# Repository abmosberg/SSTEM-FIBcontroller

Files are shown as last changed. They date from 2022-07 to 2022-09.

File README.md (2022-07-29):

# SSTEM-FIBcontroller
This is the public repository with all source files needed to reproduce the SuperSTEM FIBcontroller as presented at M&M2022.

## Notes on SuperSTEM FIBcontroller 1.0 and 1.1
The difference between revisions 1.0 and 1.1 is that in 1.0 KEY11, the bottom left button, does not work as it is connected to a pin that also connects to an LED, and thus the internal pullup behavior does not work well.
Version 1.1 attempts to fix this by moving KEY11 to D1 instead of D17.

This repository contains 3 folders, with different parts of the project:

### Arduino
Arduino sketch required to program the controller. See the Arduino help pages for instructions on how to flash. The Arduino Micro can be connected directly to a PC and flashed over the micro-USB cable.

Note, this code is still for v1.0, and is very much a rough first attempt, that can easily be refined.

### Enclosure
3D files, both Autodesk Inventor part files (configurable) and exported .stl files that can be read by any common slicer for 3D printing. For the prototype, .stl's were sliced in Ultimaker Cura and printed on an Ender 3 without supports.

### PCB
The subfolders FIBcontroller_v1.0 and v1.1 contain archived KiCad 6.0 projects. These should contain everything needed to iterate on the design, but for simple fabrication the accompanying gerber zip folders can be uploaded to any of the popular PCB manufacturing houses (e.g. PCBway, JLCPCB). v1.0 fabricated successfully to become the prototype, but no guarantees are given for v1.1
(it should only be a small change, so fairly safe)

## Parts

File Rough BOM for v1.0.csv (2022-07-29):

Type | Manufacturer | PartNo | Farnell Order Code | DigiKey PartNo | Number | Unit Price | Cost | Link
Arduino | Arduino | A000053 | 2285194 | 1050-1066-ND | 1 | £16.00 | £16.00 | https://www.digikey.co.uk/en/products/detail/arduino/A000053/4486332
Keyswitches - MX Black | Cherry | MX1A-11NW | 2292961 | CH160-ND | 14 | £0.71 | £9.91 | https://www.digikey.co.uk/en/products/detail/cherry-americas-llc/MX1A-11NW/91134
ALTERNATIVE
Keyswitches - MX Blue | Cherry | MX1A-E1NW | N/A | CH197-ND | 14 | £0.76 | £10.64 | https://www.digikey.co.uk/en/products/detail/cherry-americas-llc/MX1A-E1NW/20180
Keycaps | Adafruit | 5039 | N/A | 1528-5039-ND | 2 | £3.96 | £7.92 | https://www.digikey.co.uk/en/products/detail/adafruit-industries-llc/5039/14313478
Rotary encoder | Bourns | PEC11R-4215F-S0024 | 2474844 | PEC11R-4215F-S0024-ND | 2 | £1.66 | £3.32 | https://www.digikey.co.uk/en/products/detail/bourns-inc/PEC11R-4215F-S0024/4499665
Toggle switch | TE Connectivity ALCOSWITCH Switches | 1-1825137-6 | 3406889 | 450-2381-ND | 1 | 3.54 | 3.54 | https://uk.farnell.com/alcoswitch-te-connectivity/1-1825137-6/toggle-switch-spdt-5a-120v/dp/3406889
3-pin terminal block | Phoenix Contact | 1729131 | 1729131 |  | 1 | 0.976 | 0.976 | https://uk.farnell.com/phoenix-contact/1729131/terminal-block-wire-to-brd-3pos/dp/3041451
4-pin terminal block | Phoenix Contact | 1729144 | 3041475 |  | 1 | 1.12 | 1.12 | https://uk.farnell.com/phoenix-contact/1729144/terminal-block-wire-to-brd-4pos/dp/3041475
10k resistors | Multicomp pro | MCF 0.5W 10K | 9338373 |  | 5 | £0.06 | 0.2975 | https://uk.farnell.com/multicomp/mcf-0-5w-10k/res-10k-5-500mw-axial-carbon-film/dp/9338373
10nF axial capacitors | Vishay | MKT1813310635G | 1166871 |  | 2 | £1.05 | 2.1 | https://uk.farnell.com/vishay/mkt1813310635g/cap-0-01-f-630v-10-pet/dp/1166871
 |  |  |  |  |  | SUM: | £53.43

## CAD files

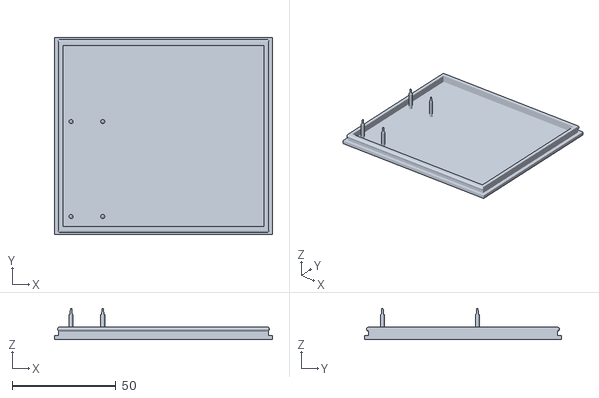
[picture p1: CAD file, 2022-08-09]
Enclosure/BARB_bottom_standalone.stl
105.0 x 95.0 x 15.0

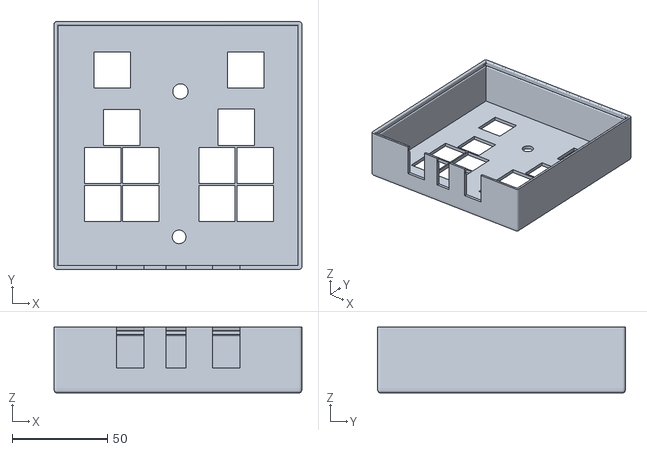
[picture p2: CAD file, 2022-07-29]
Enclosure/Enclosure_top_v2.stl
130.0 x 130.0 x 34.5

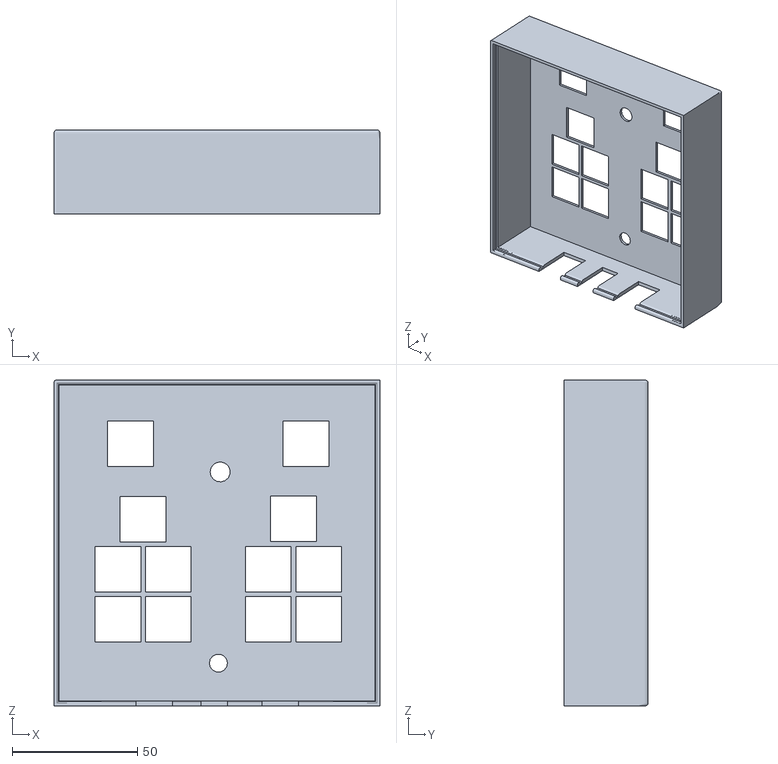
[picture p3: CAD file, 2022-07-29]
Enclosure/Enclosure_top.stl
130.0 x 33.5 x 130.0

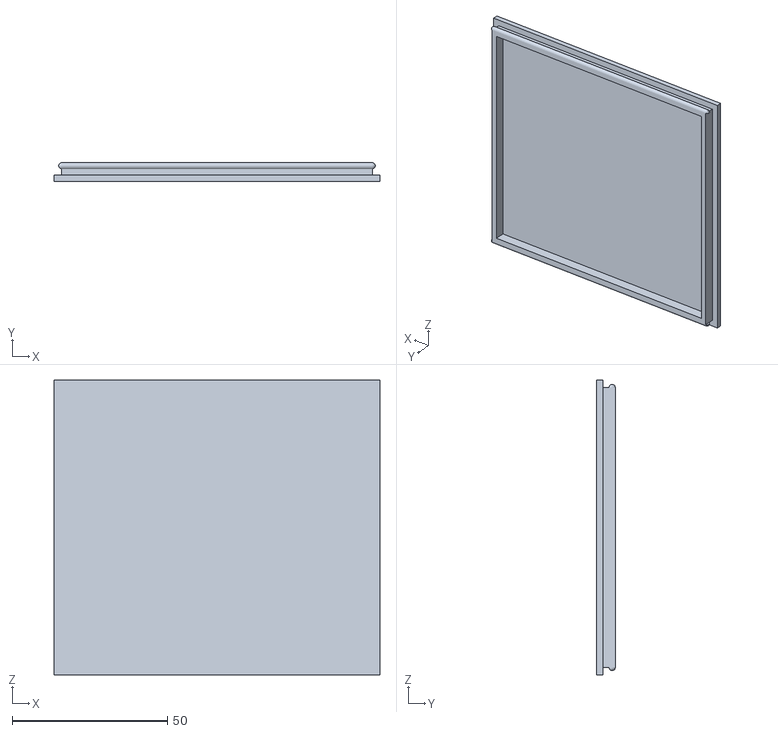
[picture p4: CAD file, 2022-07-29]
Enclosure/BRB_bottom_0.4mm_margin.stl
105.0 x 6.00 x 95.0

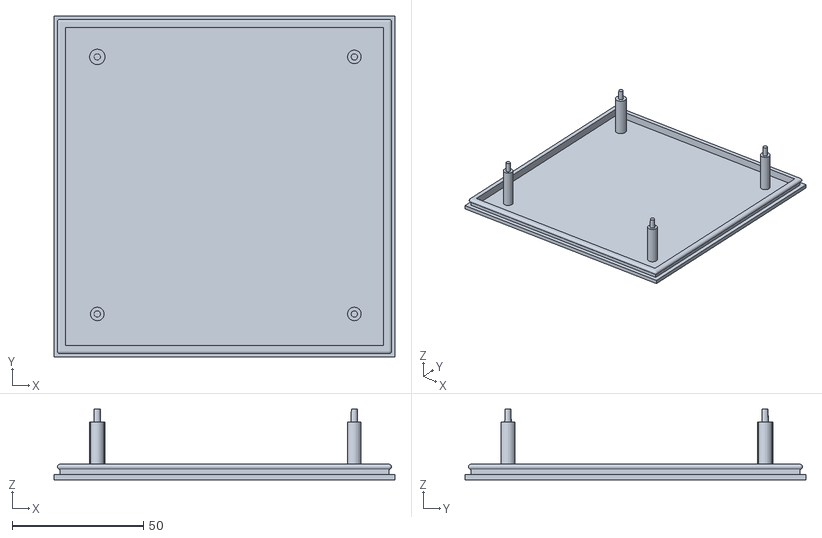
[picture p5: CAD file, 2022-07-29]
Enclosure/Enclosure_bottom_0.3mm_margin.stl
130.0 x 130.0 x 27.0

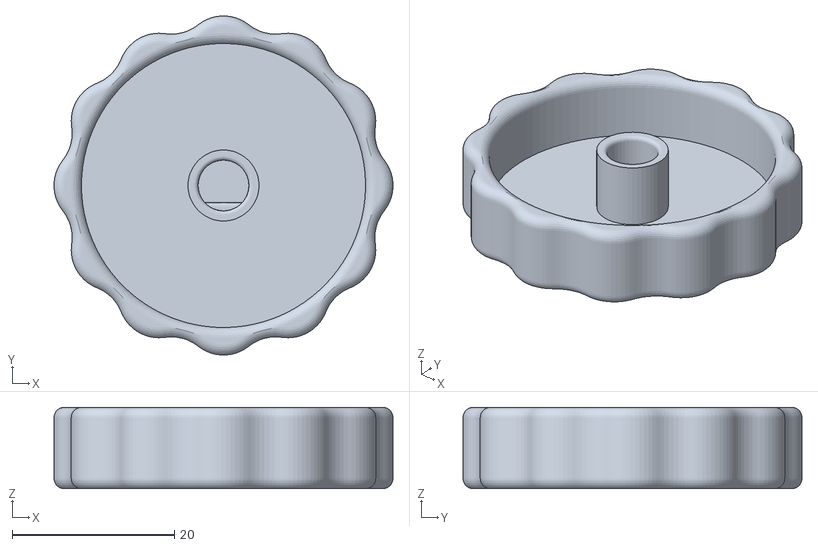
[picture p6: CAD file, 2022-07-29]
Enclosure/Encoder_wheel_10mm.stl
41.8 x 41.8 x 10.0

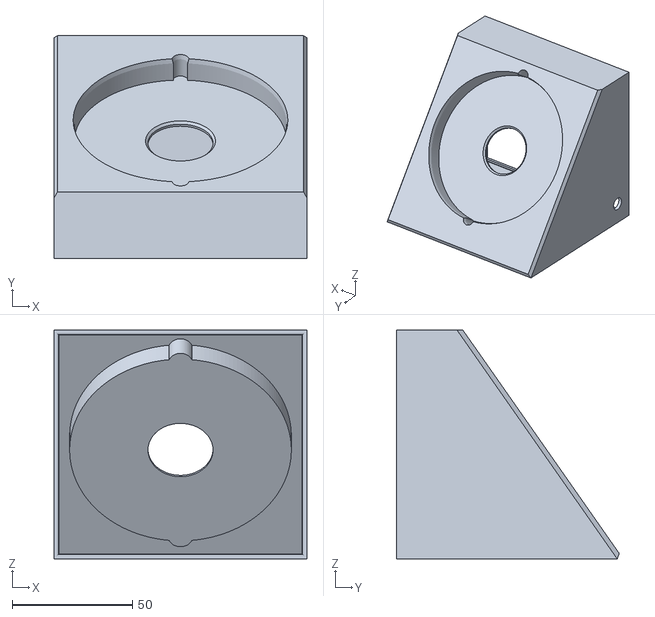
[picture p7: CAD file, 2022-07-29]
Enclosure/BRB_top.stl
105.0 x 92.4 x 95.0

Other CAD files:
Enclosure/BRB_bottom.ipt
Enclosure/BRB_bottom_standalone.ipt
Enclosure/BRB_top.ipt
Enclosure/Enclosure_bottom.ipt
Enclosure/Enclosure_top.ipt
Enclosure/Encoder_wheel.ipt

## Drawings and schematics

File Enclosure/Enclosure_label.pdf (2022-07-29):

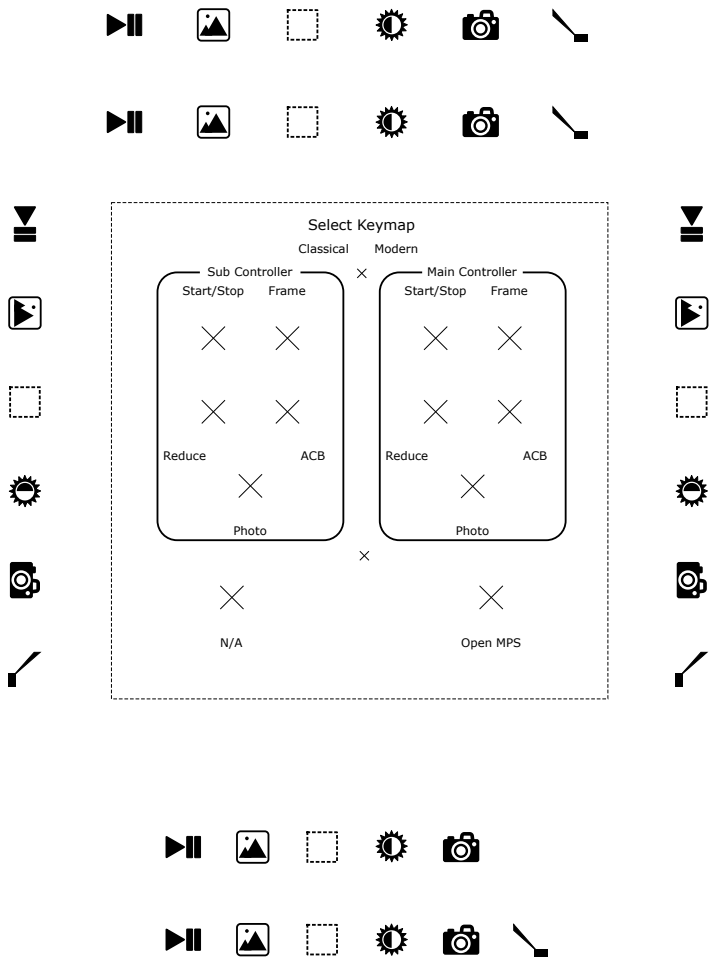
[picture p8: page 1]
Select Keymap; Classical; Modern; Sub Controller; Main Controller; Open MPS; Start/Stop; Frame; Reduce; ACB; Photo

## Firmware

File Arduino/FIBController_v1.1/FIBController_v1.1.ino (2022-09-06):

/*
  FIBcontroller
  Version 1.1

  Uses a combination of keyboard buttons, a rotary encoder and a toggle switch to send keyboard shortcuts.
  Customized here for a Hitachi NX5000, with the toggle switch used to select keyboard shortcut scheme.
  Possible schemes are Classical or Modern

  created 24 June 2022
  by Aleksander B. Mosberg, SuperSTEM

*/
#include "Keyboard.h"

// set pin numbers for keyboard switches 1-12
const int KEY1 = 7;
const int KEY2 = 8;
const int KEY3 = 20;
const int KEY4 = 21;
const int KEY5 = 5;
const int KEY6 = 6;
const int KEY7 = 22;
const int KEY8 = 23;
const int KEY9 = 4;
const int KEY10 = 14;
// No point in defining key11, pin 17 is TX LED and can't be used with internal pullup
// const int KEY11 = 17;
const int KEY12 = 15;
// pins for toggle switch
const int SW1_1 = 12;
const int SW1_3 = 11;
// pins for rotary encoder
const int RE_A = 3;
const int RE_B = 2;
const int SW2 = 16;
// pin for BRB
const int BRB = 19;

// set how long keys should be sent for before triggering releaseAll
const int press_time = 10;
// how long to wait after pressing keys to prevent debounce
const int debounce_time = 15;

int rotation;
int value;
bool submain;
char mode;
int encstate;
int oldstate;

void setup() {
  // initialize pins: KEY1-12 are all inputs using the internal pullup resistors
  // when connected these are all bridged to ground
  pinMode(KEY1, INPUT_PULLUP);
  pinMode(KEY2, INPUT_PULLUP);
  pinMode(KEY3, INPUT_PULLUP);
  pinMode(KEY4, INPUT_PULLUP);
  pinMode(KEY5, INPUT_PULLUP);
  pinMode(KEY6, INPUT_PULLUP);
  pinMode(KEY7, INPUT_PULLUP);
  pinMode(KEY8, INPUT_PULLUP);
  pinMode(KEY9, INPUT_PULLUP);
  pinMode(KEY10, INPUT_PULLUP);
  // pinMode(KEY11, INPUT_PULLUP); Pin cannot be used with internal pullup, TX LED.
  pinMode(KEY12, INPUT_PULLUP);
  // the same applies for SW1, SW2 and the BRB
  pinMode(SW1_1, INPUT_PULLUP);
  pinMode(SW1_3, INPUT_PULLUP);
  pinMode(SW2, INPUT_PULLUP);
  pinMode(BRB, INPUT_PULLUP);

  //setup serial for debugging
  // Serial.begin(9600);

  // the encoder does not use the internal pullup
  // NB: MAY HAVE TO CHANGE THIS TO MAKE RE WORK MORE RELIABLY
  pinMode(RE_A, INPUT_PULLUP);
  pinMode(RE_B, INPUT_PULLUP);

  // read initial state of encoder
  rotation = digitalRead(RE_A);
  encstate = digitalRead(RE_A) | (digitalRead(RE_B) << 1);
  oldstate = encstate;

  // set initial state of encoder action
  submain = false; // defined as false: sub controller, true: main controller

  // set up interrupts for rotary encoder
  attachInterrupt(digitalPinToInterrupt(RE_A), readencoder, CHANGE);
  attachInterrupt(digitalPinToInterrupt(RE_B), readencoder, CHANGE);

  // start emulating keyboard
  Keyboard.begin();
}

// Utility function to press buttons until they are released, with a little debounce
void buttonpress(int keypin = 0, int usbkey1 = 0, int usbkey2 = 0, int usbkey3 = 0, int dbtime = 10) {
  if (keypin != 0)
    if (usbkey1 != 0)
      Keyboard.press(usbkey1);
  if (usbkey2 != 0)
    Keyboard.press(usbkey2);
  if (usbkey3 != 0)
    Keyboard.press(usbkey3);
  delay(dbtime);
  while (digitalRead(keypin) == LOW)
    delay(dbtime);
  Keyboard.releaseAll();
  delay(dbtime);
}

void loop() {

  // first, if the BRB is pressed send the stop stage command
  if (digitalRead(BRB) == LOW) {
    buttonpress(BRB, KEY_PAUSE);
  }

  // second, check which mode/keymap we are in
  if (digitalRead(SW1_3) == LOW) {
    mode = 'c'; // classical keymap
  }
  else if (digitalRead(SW1_1) == LOW) {
    mode = 'm'; // modern keymap
  }
  else { // neither pole is shorted, switch is in center
    mode = 'o'; // neutral/'off' mode
  }

  // if the encoder wheel is pressed, toggle between sub and main magnification shortcuts
  if (digitalRead(SW2) == LOW) {
    submain = !submain;
    while (digitalRead(SW2) == LOW) {
      delay(25);
    }
    delay(debounce_time);
  }

  // 'Classical' mode
  if (mode == 'c') {
    if (digitalRead(KEY1) == LOW) { // Key1: start/stop scanning sub
      buttonpress(KEY1, KEY_LEFT_SHIFT, KEY_F12);
    }
    else if (digitalRead(KEY2) == LOW) { // Key2: single frame sub
      buttonpress(KEY2, KEY_LEFT_SHIFT, KEY_F11);
    }
    else if (digitalRead(KEY3) == LOW) { // Key3: start/stop scanning main
      buttonpress(KEY3, KEY_F12);
    }
    else if (digitalRead(KEY4) == LOW) { // Key4: single frame Main
      buttonpress(KEY4, KEY_F11);
    }
    else if (digitalRead(KEY5) == LOW) { // Key5: reduce scan sub
      buttonpress(KEY5, KEY_LEFT_SHIFT, KEY_F4);
    }
    else if (digitalRead(KEY6) == LOW) { // Key6: ACB sub
      buttonpress(KEY6, KEY_LEFT_SHIFT, KEY_F9);
    }
    else if (digitalRead(KEY7) == LOW) { // Key7: reduce scan main
      buttonpress(KEY7, KEY_F4);
    }
    else if (digitalRead(KEY8) == LOW) { // Key8: ACB main
      buttonpress(KEY8, KEY_F9);
    }
    else if (digitalRead(KEY9) == LOW) { // Key9: photo scan sub
      buttonpress(KEY9, KEY_LEFT_SHIFT, KEY_LEFT_CTRL, KEY_F11);
    }
    else if (digitalRead(KEY10) == LOW) { // Key10: photo scan main
      buttonpress(KEY10, KEY_LEFT_CTRL, KEY_F11);
    }
    // NB: KEY 11 IS DISABLED, AS THE PIN IT CONNECTS TO DRIVES AN INTERNAL LED
    // THROUGH A 1K RESISTOR MAKING THE INTERNAL PULLUP USELESS.
    // else if (digitalRead(KEY11) == LOW) { // Key11: eucentric calc display
    //   buttonpress(KEY11, KEY_F1);
    // }
    else if (digitalRead(KEY12) == LOW) { // Key12: MPS controller display
      buttonpress(KEY12, KEY_LEFT_CTRL, 51); // 51 is ASCII DEC code for '3'
    }
  }
  // If 'modern' mode
  else if (mode == 'm') {
    if (digitalRead(KEY1) == LOW) { // Key1: start/stop scanning sub
      buttonpress(KEY1, KEY_F11);
    }
    else if (digitalRead(KEY2) == LOW) { // Key2: single frame sub
      buttonpress(KEY2, KEY_LEFT_CTRL, KEY_F11);
    }
    else if (digitalRead(KEY3) == LOW) { // Key3: start/stop scanning main
      buttonpress(KEY3, KEY_F12);
    }
    else if (digitalRead(KEY4) == LOW) { // Key4: single frame main
      buttonpress(KEY4, KEY_LEFT_CTRL, KEY_F12);
    }
    else if (digitalRead(KEY5) == LOW) { // Key5: reduce scan sub
      buttonpress(KEY5, KEY_F7);
    }
    else if (digitalRead(KEY6) == LOW) { // Key6: ACB sub
      buttonpress(KEY6, KEY_LEFT_ALT, 52); // 52 is ASCII DEC code for '4'
    }
    else if (digitalRead(KEY7) == LOW) { // Key7: reduce scan main
      buttonpress(KEY7, KEY_F8);
    }
    else if (digitalRead(KEY8) == LOW) { // Key8: ACB main
      buttonpress(KEY8, KEY_LEFT_CTRL, 52); // 52 is ASCII DEC code for '4'
    }
    else if (digitalRead(KEY9) == LOW) { // Key9: photo scan sub
      buttonpress(KEY9, KEY_LEFT_SHIFT, KEY_F11);
    }
    else if (digitalRead(KEY10) == LOW) { // Key10: photo scan main
      buttonpress(KEY10, KEY_LEFT_SHIFT, KEY_F12);
    }
    // NB: KEY 11 IS DISABLED, AS THE PIN IT CONNECTS TO DRIVES AN INTERNAL LED
    // THROUGH A 1K RESISTOR MAKING THE INTERNAL PULLUP USELESS.
    // else if (digitalRead(KEY11) == LOW) { // Key11: eucentric calc display
    //   buttonpress(KEY11, KEY_LEFT_CTRL, KEY_LEFT_ALT, KEY_F1);
    // }
    else if (digitalRead(KEY12) == LOW) { // Key12: MPS controller display
      buttonpress(KEY12, KEY_LEFT_CTRL, KEY_LEFT_ALT, 51); // 51 is ASCII DEC code for '3'
    }
  }
}

// Serial printouts to put in interrupt for debugging
//    Serial.print(F("RE_A: "));
//    Serial.print(digitalRead(RE_A));
//    Serial.print(F("  RE_B: "));
//    Serial.print(digitalRead(RE_B));
//    Serial.print(F("  encstate: "));
//    Serial.print(encstate);
//    Serial.print(F("  oldstate: "));
//    Serial.println(oldstate);

void readencoder() {
  encstate = digitalRead(RE_A) | (digitalRead(RE_B) << 1);
  // at ratchet
  if (encstate == 3) {
    // Clockwise
    if (oldstate == 1) {
      if (mode == 'c') { // classical keymap
        if (submain == false) { // sub controller
          Keyboard.press(KEY_LEFT_CTRL);
          Keyboard.press(KEY_LEFT_SHIFT);
          Keyboard.press(KEY_KP_PLUS);
        }
        else { // main controller
          Keyboard.press(KEY_LEFT_CTRL);
          Keyboard.press(KEY_KP_PLUS);
        }
      }
      else if (mode == 'm') { // modern keymap
        if (submain == false) { // sub controller
          Keyboard.press(KEY_LEFT_SHIFT);
          Keyboard.press(KEY_LEFT_ALT);
          Keyboard.press(KEY_KP_PLUS);
        }
        else { // main controller
          Keyboard.press(KEY_LEFT_ALT);
          Keyboard.press(KEY_KP_PLUS);
        }
      }
      else { // mode is neither 'c' or 'm'. Should be 'n', so no action
        return;
      }
    }
    // Counterclockwise
    else if (oldstate == 2) {
      if (mode == 'c') { // classical keymap
        if (submain == false) { // sub controller
          Keyboard.press(KEY_LEFT_CTRL);
          Keyboard.press(KEY_LEFT_SHIFT);
          Keyboard.press(KEY_KP_MINUS);
        }
        else { // main controller
          Keyboard.press(KEY_LEFT_CTRL);
          Keyboard.press(KEY_KP_MINUS);
        }
      }
      else if (mode == 'm') { //modern keymap
        if (submain == false) { // sub controller
          Keyboard.press(KEY_LEFT_SHIFT);
          Keyboard.press(KEY_LEFT_ALT);
          Keyboard.press(KEY_KP_MINUS);
        }
        else { // main controller
          Keyboard.press(KEY_LEFT_ALT);
          Keyboard.press(KEY_KP_MINUS);
        }
      }
      else { // mode is neither 'c' or 'm'. Should be 'n', so no action
        return;
      }
    }
    Keyboard.releaseAll();
  }
  oldstate = encstate;
}

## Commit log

2022-08-09 Add standalone stop button
    [BARB_bottom_standalone.stl, BRB_bottom_standalone.ipt]
2022-09-06 add Arduino sketch 1.1
